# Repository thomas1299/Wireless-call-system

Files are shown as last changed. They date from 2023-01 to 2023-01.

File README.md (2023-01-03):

# Wireless-call-system
Die drahtlos angesteuerte Rufanlage dient zum Absetzen eines Notrufs, welche speziell für Menschen mit Einschränkungen der oberen Gliedmaßen entwickelt wurde. Anstatt wie bei herkömmlichen Rufanlagen, wo eine Taste gedrückt werden muss, um den Alarm auszulösen, erfolgt bei dieser Rufanlage die Alarmauslösung über Messung der Temperatur. Die Rufanlage ist in der Lage durch Messung der Temperatur zu erkennen, ob der Sensor zwischen die Lippen genommen wurde oder nicht, um so einen Alarm auszulösen. Der Alarm wird am Basisgerät, an welchem der Temperatursensor angeschlossen ist und am mobilen Empfangsgerät ausgelöst.

Die Alarmauslösung auf beiden Geräten erfolgt innerhalb von 500 ms ab dem Berühren des Sensors durch die Lippen und die Reichweite der Funkverbindung beträgt mindestens 100 m im Freien. Beide Geräte können mit einem Li-Ionen-Akku der Größe 18650 mit 3,7 V versorgt werden.

Die Rufanlage wurde so entwickelt dass diese möglichst Kostengünstig und einfach nachzubauen ist.

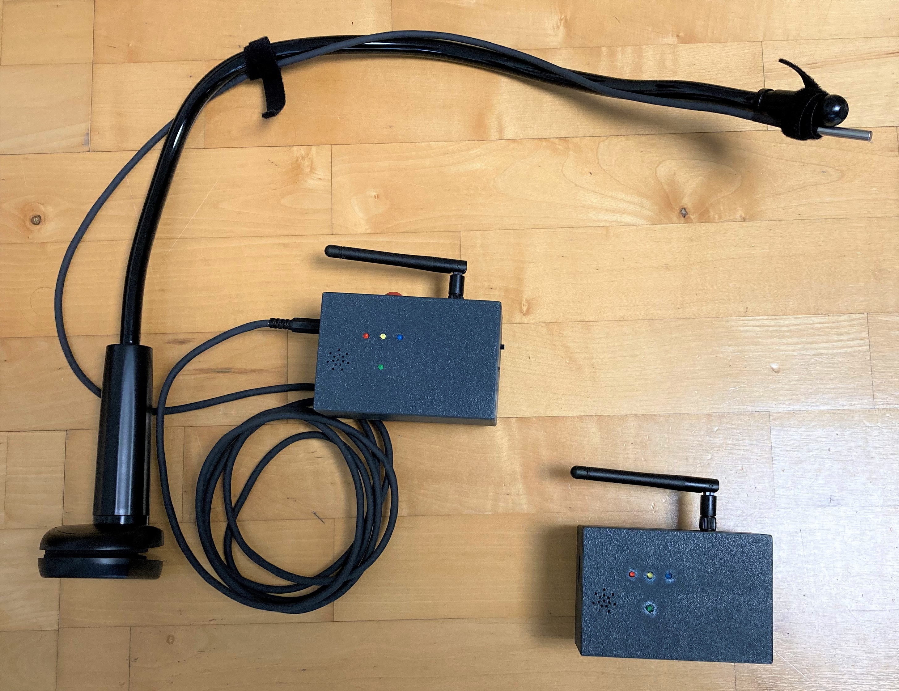
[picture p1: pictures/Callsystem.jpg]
Callsystem


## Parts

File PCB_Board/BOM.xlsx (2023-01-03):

Comment | Designator | Footprint | LCSC
Buzzer | BZ1 | Buzzer_Beeper:Buzzer_12x9.5RM7.6 | C96222
100nF | C2,C3 | Capacitor_SMD:C_0805_2012Metric | C49678
10uF | C4 | Capacitor_SMD:C_0805_2012Metric | C15850
22uF | C5,C6 | Capacitor_SMD:C_1206_3216Metric | C12891
Red | D5 | LED_SMD:LED_0805_2012Metric | C84256
Blue | D6 | LED_SMD:LED_0805_2012Metric | C34499
SS54 | D7 | Diode_SMD:D_SMA | C22452
SS34 | D8 | Diode_SMD:D_SMA | C8678
DW01A-G | IC1 | Package_TO_SOT_SMD:SOT-23-6 | C61503
TYPE-C-31-M-17 | J1 | project_library:TYPEC31M17_new | C283540
Conn_01x04_Male | J3 | Connector_PinHeader_2.54mm:PinHeader_1x04_P2.54mm_Vertical | C2905435
TP4056 | J5 | project_library:SOP127P600X175-9N | C16581
Jumper_2_Bridged | JP1 | Connector_PinHeader_2.54mm:PinHeader_1x02_P2.54mm_Vertical | C234182
22uH | L1 | project_library:SLO0630H | C207843
2N7002 | Q1 | Package_TO_SOT_SMD:SOT-23 | C8545
SI2301CDS-T1-GE3 | Q2 | Package_TO_SOT_SMD:SOT-23 | C10487
FS8205 | Q3 | Package_TO_SOT_SMD:SOT-23-6 | C908265
AO3401A | Q4 | Package_TO_SOT_SMD:SOT-23 | C15127
100k | R1,R3,R4,R17 | Resistor_SMD:R_0805_2012Metric | C149504
10k | R11 | Resistor_SMD:R_0805_2012Metric | C17414
1,2k | R12 | Resistor_SMD:R_0805_2012Metric | C17379
100 | R16 | Resistor_SMD:R_0805_2012Metric | C17408
2,2k | R18 | Resistor_SMD:R_0805_2012Metric | C17520
1M | R2 | Resistor_SMD:R_0805_2012Metric | C17514
5,1k | R5,R6,R10 | Resistor_SMD:R_0805_2012Metric | C27834
1k | R7,R8,R13,R14,R15 | Resistor_SMD:R_0805_2012Metric | C17513
4,7k | R9 | Resistor_SMD:R_0805_2012Metric | C17673
100k | RV1 | Potentiometer_THT:Potentiometer_Bourns_3296W_Vertical | C118963
SW_Push | SW1 | Connector_PinHeader_2.54mm:PinHeader_1x02_P2.54mm_Vertical | C234182
SW_SPST | SW2 | Connector_PinHeader_2.54mm:PinHeader_1x02_P2.54mm_Vertical | C234182
NRF24L01_Breakout | U1 | project_library:nRF24L01_LNA_Module | C239344
MT3608 | U4 | Package_TO_SOT_SMD:SOT-23-6 | C84817

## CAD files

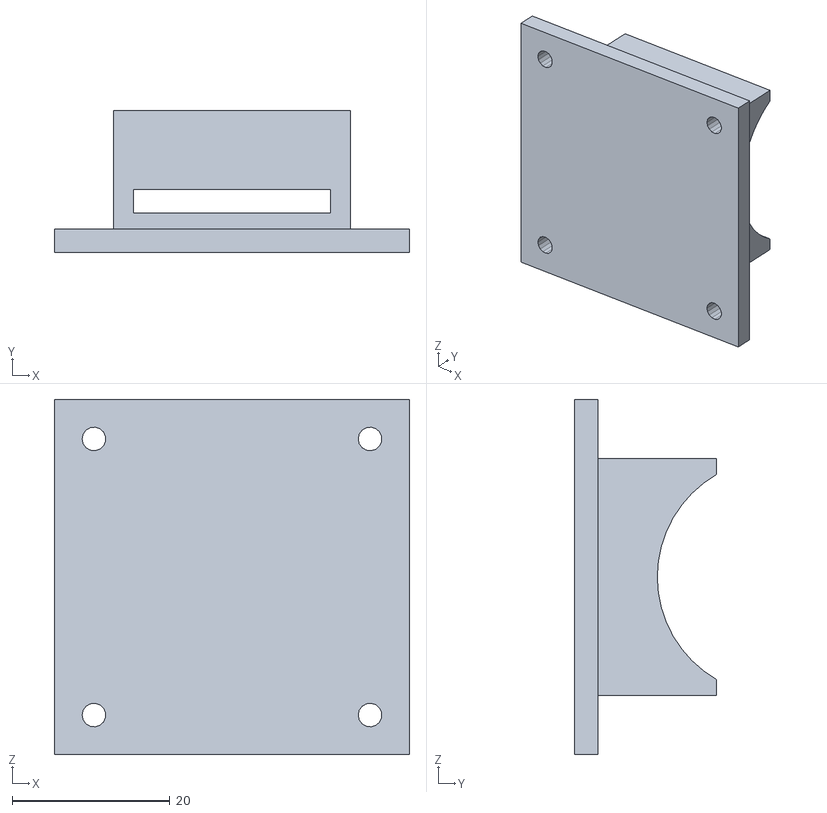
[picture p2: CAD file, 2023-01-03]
3D_Files/print_files/fastening-clip.stl
45.0 x 18.0 x 45.0

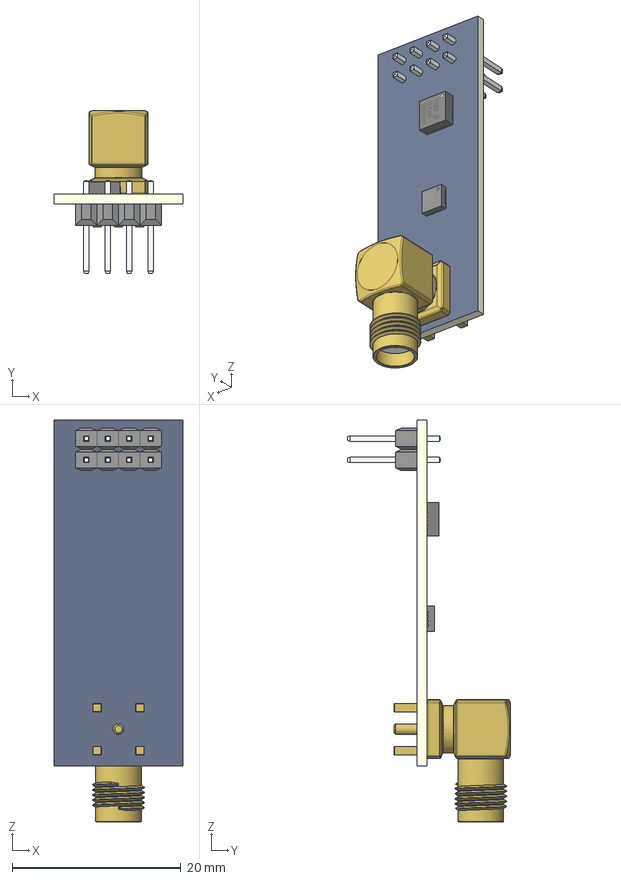
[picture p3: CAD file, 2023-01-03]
PCB_Board/project_libraries/projec_3dmodels/NRF24_module/3d-model/NRF24l01_without_antenna.stp
15.2 x 19.3 x 47.6 mm
NRF24L01_PCB
male header x 8
NRF24L01_SMA-angled
NRF24L01-CHIP-NRF___ _________
User Library-QFN-16_3x3_1
User Library-QFN-16_3x3_2
User Library-QFN-16_3x3_3
User Library-QFN-16_3x3_4
User Library-QFN-16_3x3_5
User Library-QFN-16_3x3_6
User Library-QFN-16_3x3_7
User Library-QFN-16_3x3_8
User Library-QFN-16_3x3_9
User Library-QFN-16_3x3_10
User Library-QFN-16_3x3_11
User Library-QFN-16_3x3_12
User Library-QFN-16_3x3_13
User Library-QFN-16_3x3_14
User Library-QFN-16_3x3_15
User Library-QFN-16_3x3_16
User Library-QFN-16_3x3_17
User Library-QFN-16_3x3_18

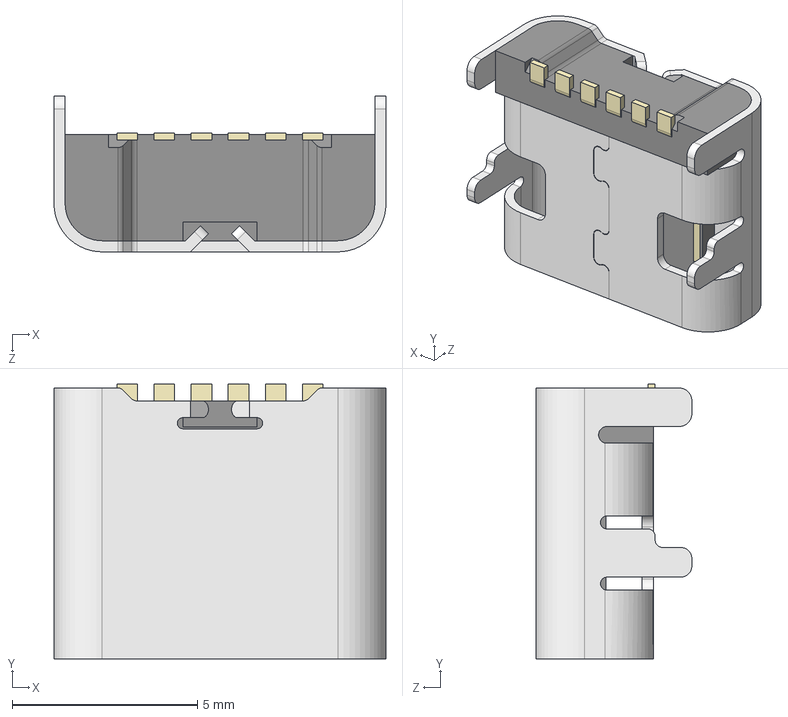
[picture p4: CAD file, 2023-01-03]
PCB_Board/project_libraries/projec_3dmodels/TYPE-C-31-M-17/TYPE-C-31-M-17.stp
8.95 x 7.40 x 4.20 mm

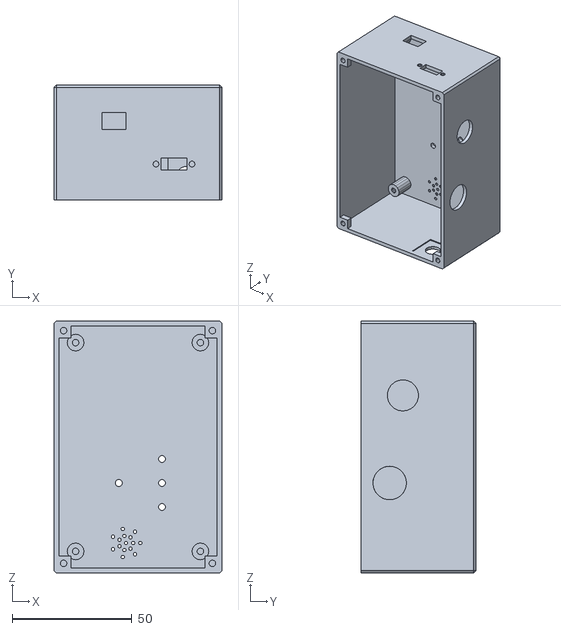
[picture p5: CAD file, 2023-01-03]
3D_Files/print_files/Top_basestation.stl
70.0 x 48.0 x 105.0

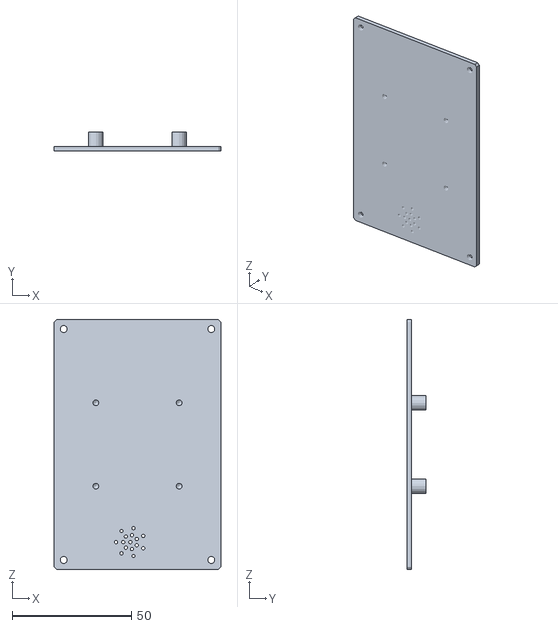
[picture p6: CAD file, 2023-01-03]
3D_Files/print_files/Case_bottom.stl
70.0 x 8.00 x 105.0

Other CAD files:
3D_Files/print_files/Top_handheld.stl
3D_Files/Case_bottom.ipt
3D_Files/Top_basestation.ipt
3D_Files/Top_handheld.ipt
3D_Files/fastening-clip.ipt
PCB_Board/project_libraries/projec_3dmodels/NRF24_module/3d-model/NRF24l01_without_antenna.iam

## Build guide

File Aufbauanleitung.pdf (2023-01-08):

# Aufbauanleitung der Rufanlage

## Inhalt

Dies ist eine Schritt-für-Schritt-Anleitung, um die drahtlos angesteuerte Rufanlage, bestehend aus dem Basisgerät und dem Empfangsgerät, nachbauen zu können. Der Schaltplan der Platine (Callsystem.pdf) befindet sich im Ordner „PCB_Board“.

### 1. Werkzeugliste

Zum Aufbau der Rufanlage werden folgende Werkzeuge benötigt:
- Lötkolben + Lötzinn
- Seitenschneider
- Flachzange oder Kombizange
- Heißklebepistole
- Multimeter
- Heißluftfön (alternativ Feuerzeug)
- Evtl. Bohrmaschine
- Kreuzschlitzschraubendreher PZ1

### 2. Bauteilliste

Folgende Komponenten sind erforderlich, für den Nachbau der drahtlos angesteuerte Rufanlage:

Teil | Lieferant | Bestellnummer | Stück
Arduino Nano | Amazon | Amazon-Link (https://www.amazon.de/AZDelivery-Atmega328-gratis-Arduino-kompatibel/dp/B078SBBST6?adgrpid=73713830840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) | 2
Bestückte Platine (PCB) | JLCPCB | https://jlcpcb.com/ | 2
18650 Akkuhalterung | Amazon | Amazon-Link (https://www.amazon.de/Haljia-18650-Batterie-Halterung-Kunststoff-Stift/dp/B07MM1NHHL?__mk_de_DE=%C3%85M%C3%85%C5%BD%C3%95%C3%91) | 2
Li-Ion Akku 18650 3,7V-3000mAh | Amazon | Amazon-Link (https://www.amazon.de/Wiederaufladbarer-POWO18B-Knopfbatterien-Taschenlampe-batteriebetriebene-Red/dp/B09KZGQSJJ) | 2
RF24L01+PA+LNA-Funkmodul | Amazon | Amazon-Link (https://www.amazon.de/-/en/DollaTek-2-Piece-NRF24L01-Antistatic-Compatible/dp/B07PQPFTWZ) | 2
Schiebeschalter | Amazon | Amazon-Link (https://www.amazon.de/-/en/gp/product/B07Z4RW9X6/ref=ppx_od_dt_b_asin_title_s00?ie=UTF8&psc=1) | 2
Klettband | Conrad | 536744 – U3 | 2

LED Rot 3mm | Conrad | 1603079 – U3 | 2
LED Gelb 3mm | Conrad | 1577458 – U3 | 2
LED Blau 3mm | Conrad | 1577321 – U3 | 2
LED Grün 3mm | Conrad | 1577354 – U3 | 2
Buchsenleiste 15-polig | Conrad | 1492307 – U3 | 4
4-poliger 3,5mm Klinkenstecker | Amazon | Amazon-Link (https://www.amazon.de/gp/product/B08DTC33XC/ref=ppx_od_dt_b_asin_title_s03?ie=UTF8&psc=1) | 1
4-poliger 3,5mm Klinkensteckerbuchse | Amazon | Amazon-Link (https://www.amazon.de/gp/product/B089222S84/ref=ppx_od_dt_b_asin_title_s03?ie=UTF8&psc=1) | 1
TSic506 Temperatursensor | Conrad | 506360 – U3 | 1
Edelstahlhülse | Conrad | 156557 – U3 | 1
4-poliges Kabel (2 Meter) | Conrad | 457980 – U3 | 1
Wärmeleitkleber | Amazon | Amazon-Link (https://www.amazon.de/gp/product/B00XQ9AZ8Y/ref=ppx_od_dt_b_asin_title_s00?ie=UTF8&th=1) | 1
Schwanenhals | Amazon | Amazon-Link (https://www.amazon.de/gp/product/B00XQ9AZ8Y/ref=ppx_od_dt_b_asin_title_s00?ie=UTF8&th=1) | 1
Taster | Amazon | Amazon-Link (https://www.amazon.de/gp/product/B0825RCZJS/ref=ppx_od_dt_b_asin_title_s01?ie=UTF8&psc=1) | 1
Schrumpfschlauch ø 2,5 mm | Conrad | 1572501 - U3 | 0,2
Schrumpfschlauch ø 5 mm | Conrad | 1571367 - U3 | 0,2
Schrauben ISO7049 2,9x9,5mm | Conrad | 147586 – U3 | 24
Schaltdraht ø0,2mm² verschiedene Farben | Conrad | 1567887 - U3 | 5m

Folgende Teile aus dem Ordner (3D_Files\print_files) müssen mit einem 3D-Drucker ausgedruckt werden:
Teil | Stück
Case_bottom | 2
Top_basestation | 1
Top_handheld | 1
Fastening-clip | 2

### 3. Leiterplattenbestellung

Für beide Geräte wurde eine Platine entwickelt, die in beiden Geräten eingebaut wird. Die vorbestückte Platine muss von einem Leiterplattenhersteller produziert werden. Vorzugsweise sollte die Platine beim Hersteller „JLCPCB“ (https://jlcpcb.com/) bestellt werden, weil die im Projektordner enthaltene Bauteilliste auf dem Teilekatalog dieses Herstellers basiert. Sollte die Platine bei einem anderen Hersteller bestellt werden, so ist darauf zu achten, dass die Bauteilliste (BOM) des Projektes auf die verfügbaren Bauteile dieses Herstellers angepasst werden.

Um die Platine bestellen zu können, werden folgende Dateien aus dem Ordner „PCB_Board“ benötigt:
- Gerber.zip (Gerber-Dateien)
- BOM.xlsx (Bauteilliste inkl. Teilenummer)
- CPL.xlsx

Bestellablauf:
1. Zuerst einen Account bei JLCPCB erstellen (https://jlcpcb.com/)

2. Nachdem der Account erstellt wurde, klicken Sie auf die Schaltfläche „Order now“.
3. Auf die blaue Schaltfläche „Add Gerber File“ klicken und das Archiv „Gerber.zip“ hochladen. Nach dem Hochladen wird die Platine am Bildschirm angezeigt. Nun weiter nach unten scrollen bis zum „PCB-Assembly“; die Einstellungen müssen nicht angepasst werden.

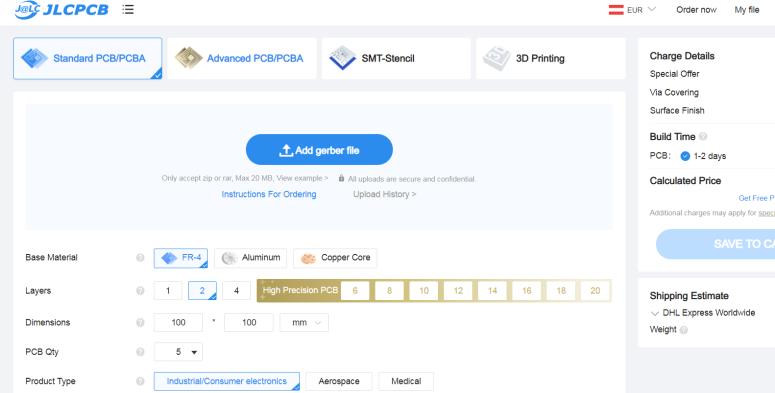
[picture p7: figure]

4. Die Schaltfläche für „PCB-Assembly“ aktivieren (roter Pfeil im Bild). Wenn alle Einstellungen wie im Bild aktiviert sind, drücken Sie auf die Schaltfläche „Confirm“.

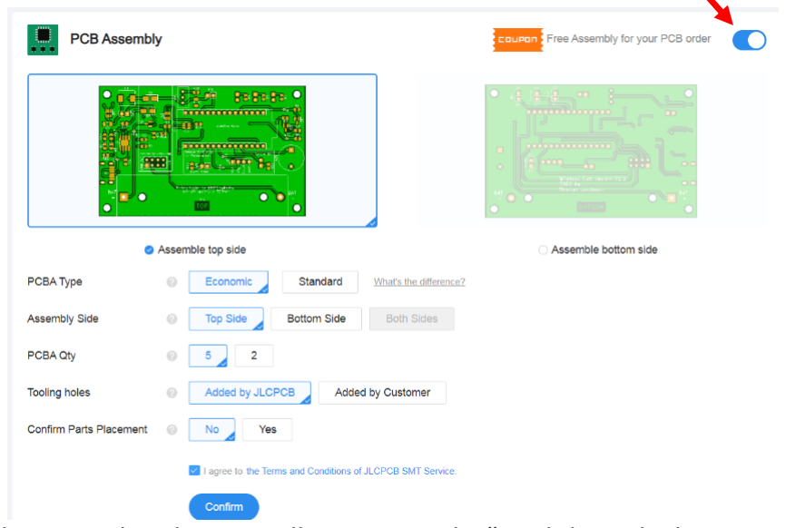
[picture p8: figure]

5. Im nächsten Schritt werden die Bauteilliste „BOM.xlsx“ und die Bohrdatei „CPL.xlsx“ aus dem Projektordner „PCB_Board“ hochgeladen.
6. Im Anschluss muss eine Beschreibung für das Produkt eingegeben werden. Dazu die Kategorien „Research\Education\DIY\Entertainment“ und „Others“ auswählen und eine kurze Beschreibung eintippen ( z.B. Rufanlage). Um fortzufahren klicken Sie auf die Schaltfläche „Next“.

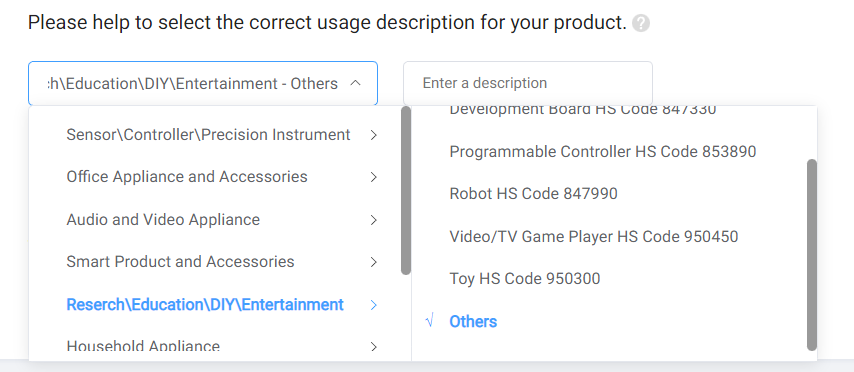
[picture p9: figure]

7. Im nächsten Schritt werden alle Bauteile aus der Bauteilliste aufgelistet; sollten keine Fehler angezeigt werden, kann zum nächsten Schritt übergegangen werden. Sollten etwaige Bauteile nicht mehr verfügbar sein, müssen andere Bauteile verwendet werden. Dazu muss die Bauteilliste „BOM.xlsx“ geändert werden. Um alternative Bauteile auswählen zu können, müssen diese im Teilekatalog des Herstellers gesucht und die Bauteilenummer (LCSC-Nummer) in die Bauteilliste eingetragen werden. Zum Aktualisieren der neuen Bauteile muss Schritt 6 wiederholt werden.
8. In diesem Schritt wird die Platine mit platzierten Komponenten und den gesamten Kosten angezeigt. Sollten die Komponenten nicht ordentlich platziert worden sein, können diese mit einem Klick auf die rot eingekreiste Schaltfläche automatisch angeordnet werden. Mit einem Klick auf „Save to Cart“ wird die Platine mit den Komponenten in den Einkaufswagen gelegt.

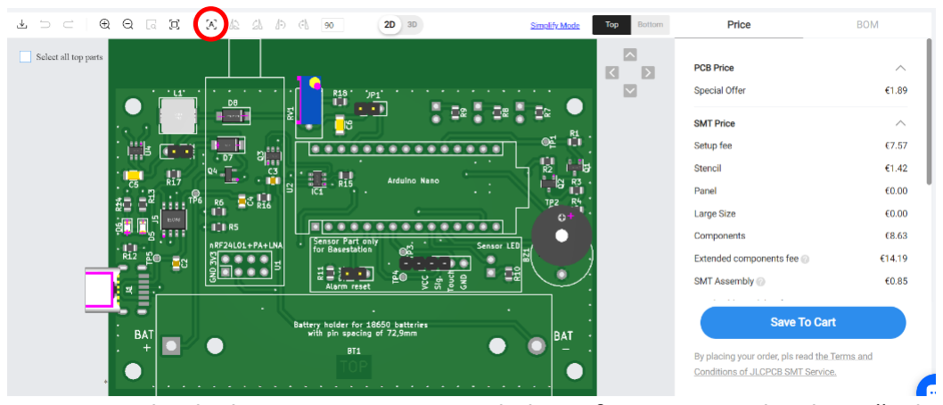
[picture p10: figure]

9. Im geöffneten Warenkorb kann mit einem Klick auf „Secure Checkout“ die Bestellung abgeschlossen werden.

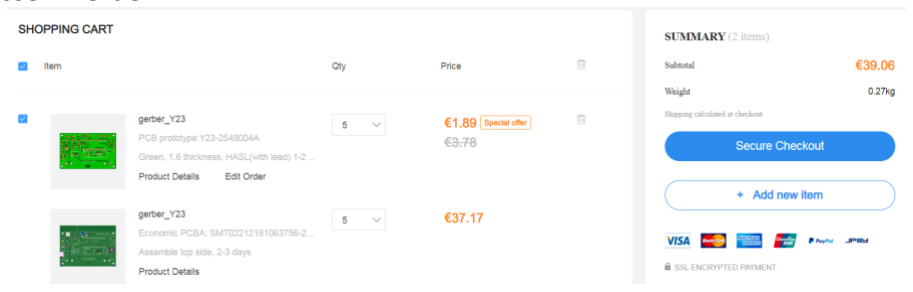
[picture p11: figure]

### 4. Programmieren beider Mikrocontroller 4.1. Vorbereitungen der Entwicklungsumgebung

1) Downloaden und Installieren der aktuellen Arduino IDE https://www.arduino.cc/en/software
2) Die Arduino Entwicklungsumgebung starten
3) Installieren der benötigten Librarys
- Tools > Manage Libraries…
- Nach „RF24“ suchen und die Library von TMRh20 installieren

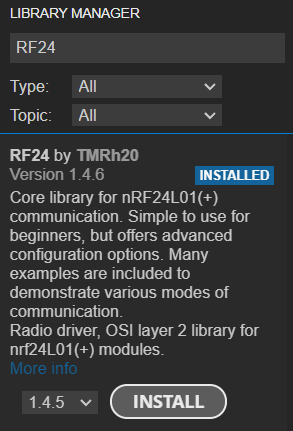
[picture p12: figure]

4) Die Ordner der Firmware für beide Geräte aus dem Repository downloaden.
- SW_Basestation
- SW_Handheld

### 4.2. Programmierung der Mikrocontroller

Zum Programmieren der beiden Arduino Nanos wird ein USB-Kabel mit USB-Mini-B-Stecker benötigt. Der Ablauf der Programmierung erfolgt für beide µC gleich, jedoch werden unterschiedliche Firmwares für die beiden Geräte verwendet.

1) Öffnen der SW_Basisstation.ino bzw. SW_Handheld.ino Firmware
2) Board aus der Boardliste auswählen
- Tools>Board> Arduino AVR Boards > Arduino Nano

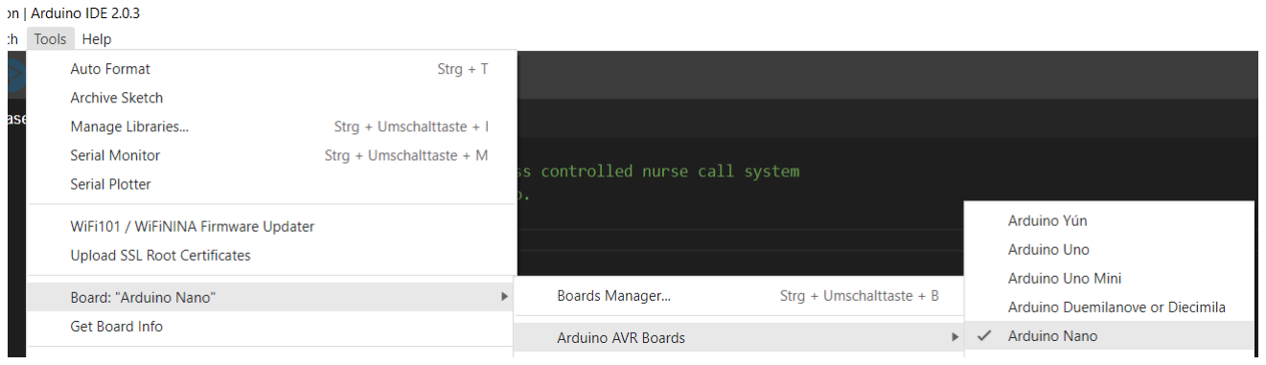
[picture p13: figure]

3) Arduino über ein USB-Kabel mit dem Computer verbinden und den Port auswählen.
- Tools > Port > „Port“ (Portnummer kann unterschiedlich sein)
4) Mit einem Klick auf „Verify“ prüfen, ob die Firmware kompiliert werden kann.
5) Mit Klick auf den „Upload“ Button wird die Firmware auf dem Arduino programmiert.

Nach dem Programmieren kann der Arduino vom Computer getrennt und auf die Platine gesteckt werden.

### 5. Aufbau der Rufanlage

Nachdem alle benötigten Teile geliefert worden sind, kann mit dem Aufbau der Rufanlage begonnen werden. Der prinzipielle Aufbau beider Geräte ist identisch, jedoch werden beim Basisgerät zusätzlich ein Taster sowie die Klinkensteckerbuchse für den Sensor eingebaut.

Um Energie während des Betriebs zu sparen, wird auf beiden Mikrocontrollern der Vorwiderstand der Power LED ausgelötet (siehe rot markierter Bereich im folgenden Bild).

Schritt 1) Zuerst werden die beiden Buchsenleisten und danach die Akkuhalterungen auf die Platinen gelötet.

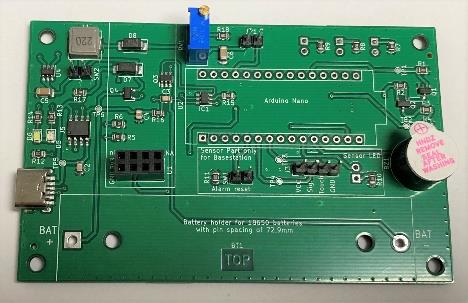
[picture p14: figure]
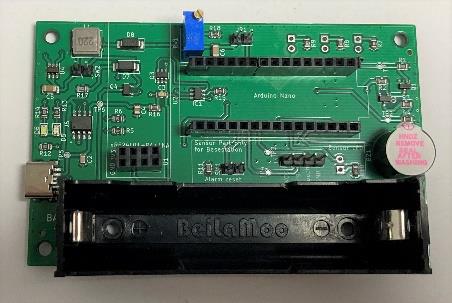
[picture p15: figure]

Schritt 2) Alle 4 LEDs (blau, gelb, grün, rot) müssen für den Einbau in das Gehäuse vorbereitet werden, damit die Anschlussdrähte keinen Kurzschluss auf der Platine verursachen. Für die elektrische Verbindung müssen 8 Drähte (4x rot / 4x schwarz) mit je einer Länge von 17 cm vorbereitet werden. Zuerst wird mit einer Zange die Kathode (kürzeres Bein „-“Pol) bei jeder LED umgebogen. Die umgebogenen Beine werden kurz nach der Biegung abgetrennt und dort die schwarzen Drähte angelötet. Der andere Anschluss, die Anode, der LED, wird in die gegenüberliegende Richtung gebogen und ebenfalls gekürzt. An diesen Anschlüssen werden die roten Drähte angelötet.

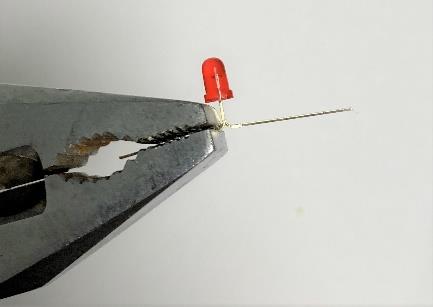
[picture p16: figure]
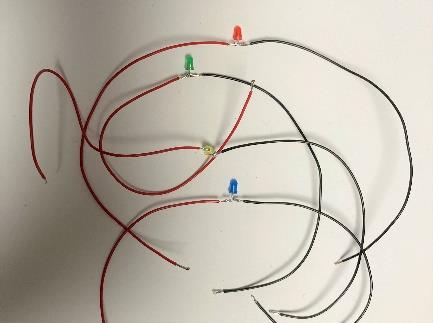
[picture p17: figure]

Schritt 3) Die Anschlussdrähte der LEDs werden nun an die Unterseite der Platine gelötet, dabei sollte die Beschriftung auf der Platine beachtet werden.

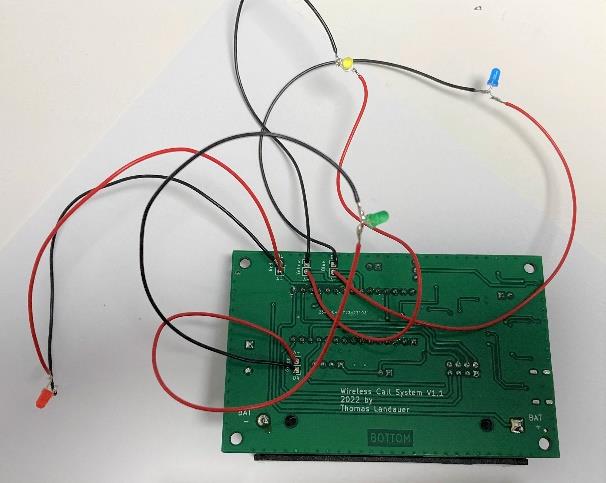
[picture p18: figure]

Schritt 4) In diesem Schritt werden nun die LEDs in das Gehäuse an die vorgesehene Position gesetzt und mit der Heißklebepistole fixiert. Sollten die LEDs nicht in die Löcher passen, muss dieses mit einem 3 mm Bohrer aufgebohrt werden. Beim Einkleben ist darauf zu achten, dass die Anschlussdrähte vollständig vom Kleber bedeckt sind. Die Reihenfolge, in der die LEDs von links beginnend eingeklebt werden, ist: rot, gelb, blau. Nachdem die LEDs eingeklebt sind, kann die Platine in das Gehäuse gesetzt und mit 4 Schrauben festgeschraubt werden.

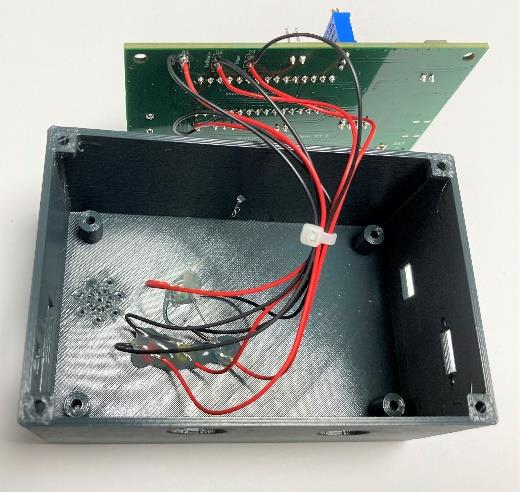
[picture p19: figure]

Schritt 5) Jetzt wird der Ein- und Ausschalter für den Einbau vorbereitet. Dazu werden 2 Drähte mit je 7 cm Länge wie im Bild dargestellt an 2 Anschlüsse des Schalters gelötet.

Die beiden Drahtenden werden anschließend auf die Stiftleiste mit der Bezeichnung „SW2“ gelötet. Nach dem Löten wird der Schalter mit der Heißklebepistole an die Wand des Gehäuses geklebt.

Sobald der Ein- und Ausschalter in das Gehäuse geklebt wurde, ist der Aufbau des Empfängergerätes abgeschlossen.

Alle weiteren Schritte betreffen nur das Basisgerät.

Schritt 6) Für den Einbau der Klinkenstecker-Buchse werden 3 Drähte mit einer Länge von 7 cm benötigt. Die Drähte werden entsprechend dem Schaltplan an die Klinkenstecker-Buchse (J2) angelötet. Um ein Vertauschen der Anschlüsse zu vermeiden, sollte der Klinkenstecker in die Buchse gesteckt und mit einem Multimeter durchgemessen werden. Nachdem die Drähte an die Buchse gelötet wurden, kann die Klinkenstecker-Buchse in das Gehäuse eingebaut und die Drähte an die Stiftleiste J3 gelötet werden. Sollte die Buchse nicht in die Öffnung im Gehäuse passen, so muss diese mit einem geeigneten Bohrer aufgebohrt werden.

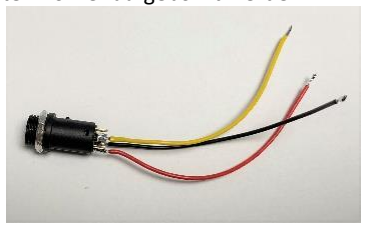
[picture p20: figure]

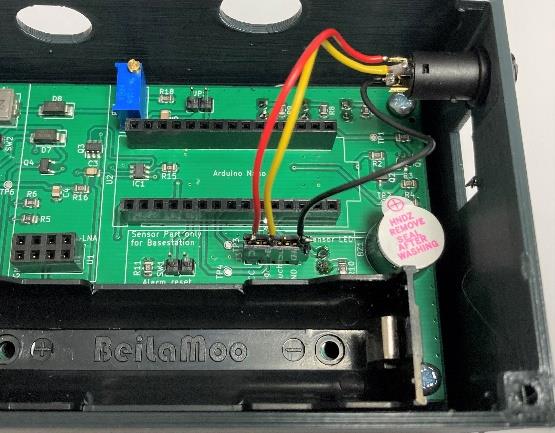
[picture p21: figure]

Schritt 7) In diesem Schritt erfolgt der Einbau des Tasters. Zuerst wird der Taster zerlegt und beide Drähte auf 8 cm gekürzt. Anschließend wird der Taster am Gehäuse befestigt und danach werden die Drähte an die Stiftleisten mit der Bezeichnung SW1 gelötet. Somit sind nun beide Platinen vollständig bestückt.

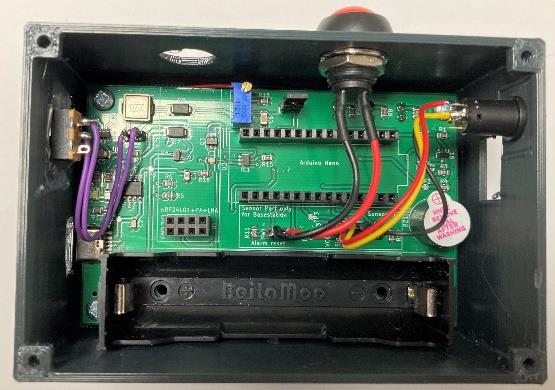
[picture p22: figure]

### 5.1. Einkleben des Sensors

Damit der Sensor verwendet werden kann, muss dieser zunächst in eine Edelstahlhülse geklebt und an ein Kabel gelötet werden. Die Länge des Kabels kann individuell festgelegt werden. Eine Länge von 2-3 Metern ist ausreichend.

Für die Montage des Sensors werden folgende Teile benötigt:
- TSic506-Sensor
- Edelstahlhülse
- Wärmeleitkleber
- Klinkenstecker
- Kabel
- Schrumpfschläuche

Schritt 1) Zuerst den Klinkenstecker zerlegen und den Knickschutz auf das Kabel schieben. Danach den Mantel des Kabels auf einer Länge von max. 1 cm abisolieren (die einzelnen Drähte
sollten | möglichst | kurz | sein, | da | ansonsten | der | Einbau | schwieriger | wird).
Den Kabelschirm entflechten, auf eine Seite führen und dann verdrillen. Im Anschluss 3 Drähte abisolieren und verzinnen; der vierte Draht kann abgeschnitten werden, weil dieser nicht benötigt wird. Danach den verdrillten Kabelschirm durch die Bohrung des Steckers führen, umknicken und dann verlöten. Die Zugentlastungslaschen des Klinkensteckers müssen den Mantel vollständig überdecken (roter Kreis in den Bildern)!

Danach die 3 Drähte entsprechend dem Schaltplan an die Laschen des Klinkensteckers löten.

Nach dem Löten die einzelnen Leitungen mit einem Durchgangsprüfer auf Kurzschlüsse überprüfen! Wenn keine Kurzschlüsse vorhanden sind, können die Zugentlastungslaschen mit einer Zange auf das Kabel gepresst werden und im Anschluss der Knickschutz wieder angeschraubt werden.

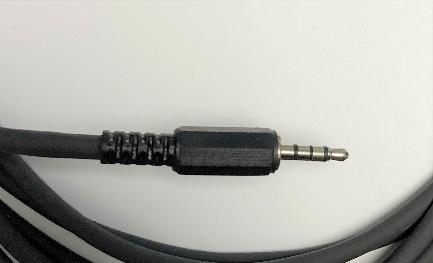
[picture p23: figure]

Schritt 2) Nun wird der Sensor an das Kabel gelötet. Dazu muss ebenfalls der Mantel des Kabels auf einer Länge von ca. 1 cm abisoliert werden. Der Kabelschirm und der nicht benötigte Draht können abgeschnitten werden. Die Anschlussdrähte des Sensors werden ebenfalls gekürzt. Die beiden größeren Schrumpfschläuche werden vor der Montage auf das Kabel geschoben. Danach
werden | die | einzelnen | Drähte | abisoliert | und | mit | Lötzinn | verzinnt.
Bevor mit dem Löten des Sensors begonnen wird, sollte die korrekte Verkabelung mit einem Multimeter (Durchgangsprüfer) überprüft werden. Dazu das Kabel am Basisgerät einstecken und mit dem Multimeter auf der Platine (Stifleiste J3) und am Kabelende auf Durchgang prüfen. Das Ergebnis der Messung auf einem Blatt notieren.

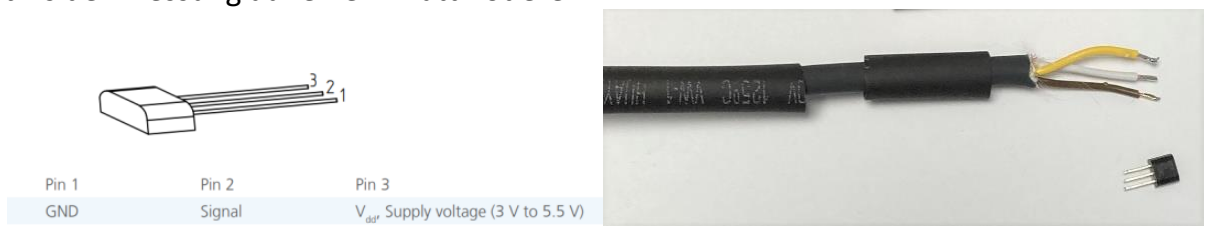
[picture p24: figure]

Bevor der Sensor an das Kabel gelötet werden kann, muss auf jedem Kabel ein kurzes Stück Schrumpfschlauch aufgeschoben werden. Danach kann der Sensor entsprechend der Schaltung und dessen Anschlussbelegung auf das Kabel gelötet werden. Nach dem Löten werden die Schrumpfschläuche über die Lötstellen geschoben und mit einem Heißluftfön oder vorsichtig mit einem Feuerzeug aufgeschrumpft. Im Anschluss wird der ø 2,5 mm Schrumpfschlauch wie im Bild dargestellt nach vorne gezogen und ebenfalls geschrumpft. Dieser Schrumpfschlauch ist nötig, damit das Kabel besser in der Edelstahlhülse sitzt.

Schritt 3) In diesem Schritt erfolgt das Einkleben des Sensors. Bevor mit dem Einkleben begonnen werden kann, wird der Schrumpfschlauch mit ø 5 mm über das Kabel gezogen. Im

Anschluss wird die Edelstahlhülse bis zur Hälfte mit dem Wärmeleitkleber befüllt. Nach dem Befüllen der Hülse wird der Sensor in die Hülse hineingeschoben, bis dieser den Boden der Hülle berührt. Nun muss circa 30 Minuten gewartet werden, bis der Kleber ausgehärtet ist; dabei sollte der Sensor nicht bewegt werden. Am besten ist es, wenn die Hülse und das Kabel mit Klebeband fixiert werden. Nachdem der Kleber ausgehärtet ist, kann der Schrumpfschlauch über Hülse und Kabel geschoben und geschrumpft werden. Dieser Schrumpfschlauch bietet zusätzlichen Schutz gegen Knicken und das Eindringen von Wasser.

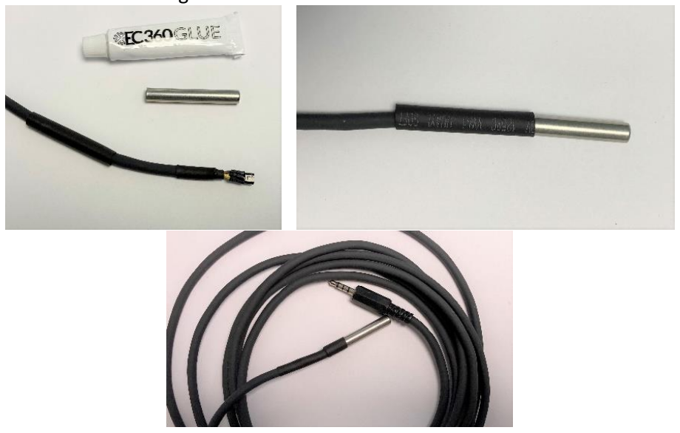
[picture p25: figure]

### 5.2. Einstellen des Step-Up-Converters

Bevor der Mikrocontroller und das Funkmodul eingesetzt werden können, muss die Spannung des Step-Up-Converters bei beiden Geräten eingestellt werden. Dazu muss der Akku richtig eingesetzt werden. Der Pluspol des Akkus auf der Seite des Ein- und Ausschalters und der Minuspol auf der Seite des Buzzers. Nachdem der Akku eingesetzt ist, muss das Gerät über den Ein- und Ausschalter eingeschaltet werden.
Mit einem Multimeter wird nun die Spannung am linken Pin von der Stiftleiste JP1 gegen Masse (GND) gemessen. Nun wird mit einem Schraubendreher der Widerstand des Potentiometers verändert, bis das Multimeter 5 V anzeigt (gegen den Uhrzeigersinn, um die Spannung zu erhöhen, im Uhrzeigersinn, um die Spannung zu verringern).
Nachdem die Spannung auf 5 V eingestellt ist, können die beiden Pins von der Stiftleiste JP1 durch Löten verbunden werden.

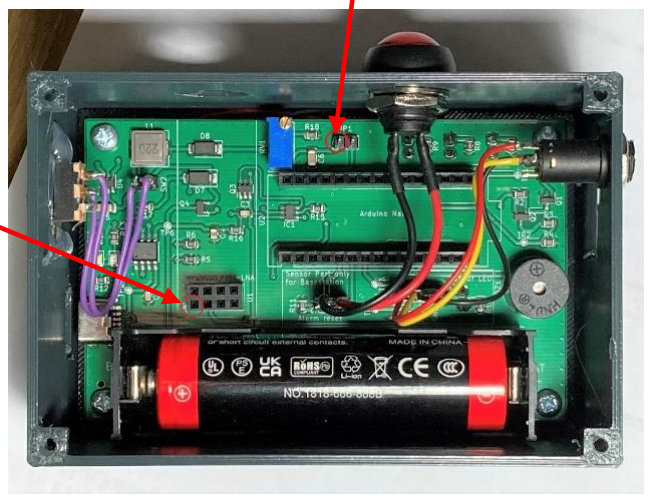
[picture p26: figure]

### 5.3. Einsetzen des Arduinos und des Funkmoduls

Nachdem bei beiden Geräten der Step-Up-Converter eingestellt wurde, können die Mikrocontroller und die nRF-Funkmodule eingesteckt werden.

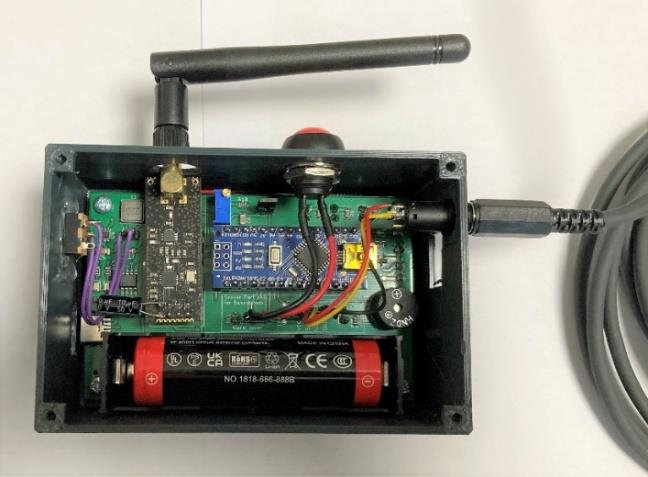
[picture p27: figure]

Nach dem Einsetzen der Komponenten kann das Gehäuse geschlossen werden. Dazu werden je Gerät 8 Stk. Schrauben und der gedruckte Gehäuseboden sowie der Befestigungsclip benötigt. Bei der Positionierung des Bodens ist darauf zu achten, dass die Bohrungen für den Buzzer über diesem sind. Der Befestigungsclip kann wie unterhalb im linken Bild dargestellt oder um 90 ° gedreht montiert werden. Am Ende wird noch die Antenne auf das Funkmodul geschraubt.

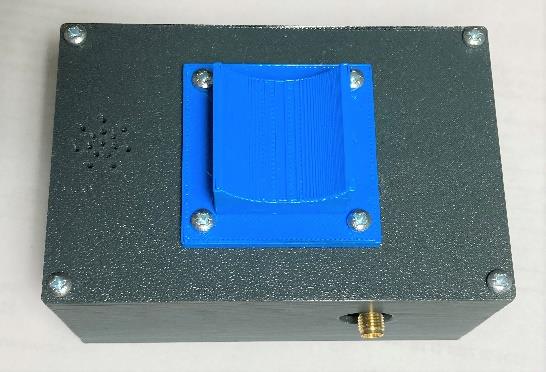
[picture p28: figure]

### 6. Montage am Bett

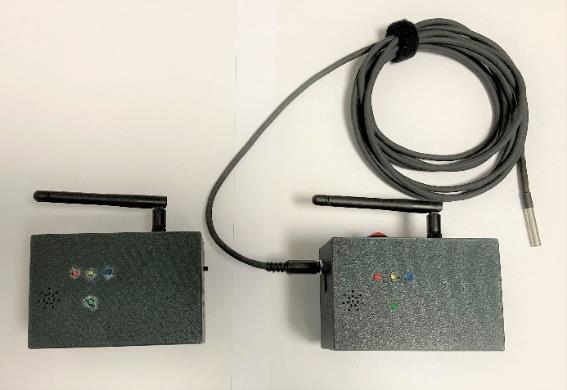
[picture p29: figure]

Das Kabel des Sensors kann wie unten im Bild dargestellt mittels Klettverschlüssen oder z.B. Kabelbindern am Schwanenhals befestigt werden. Der Schwanenhals selbst wird mit dessen Befestigungsgriff am Bett so befestigt, dass der Sensor in die Nähe des Mundes gebracht werden kann. Das Basisgerät kann über den Befestigungsclip und Klettverschluss am Bettgestänge angebracht werden.

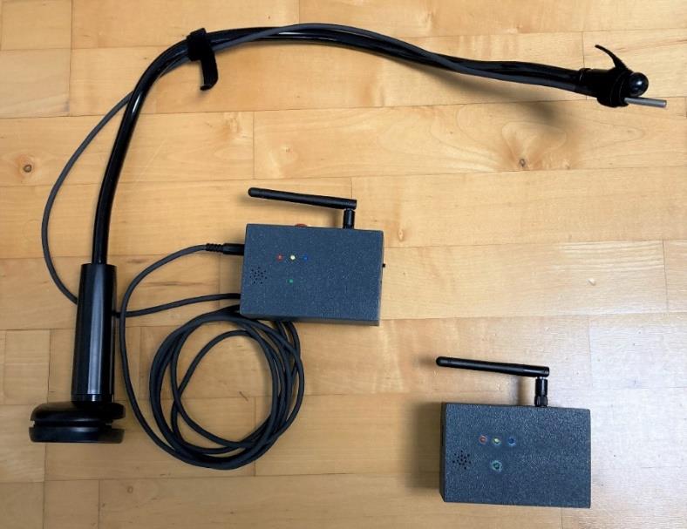
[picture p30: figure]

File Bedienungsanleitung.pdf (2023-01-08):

# Bedienungsanleitung

## Inhalt

Die drahtlos angesteuerte Rufanlage dient zum Absetzen eines Notrufs, welche speziell für Menschen mit Einschränkungen der oberen Gliedmaßen entwickelt wurde. Anstatt wie bei herkömmlichen Rufanlagen, wo eine Taste gedrückt werden muss, um den Alarm auszulösen, erfolgt bei dieser Rufanlage die Alarmauslösung über Messung der Temperatur. Die Rufanlage ist in der Lage durch Messung der Temperatur zu erkennen, ob der Sensor zwischen die Lippen genommen wurde oder nicht, um so einen Alarm auszulösen. Der Alarm wird am Basisgerät, an welchem der Temperatursensor angeschlossen ist und am mobilen Empfangsgerät ausgelöst.

Die Alarmauslösung auf beiden Geräten erfolgt innerhalb von 500 ms ab dem Berühren des Sensors durch die Lippen und die Reichweite der Funkverbindung beträgt mindestens 100 m im Freien. Beide Geräte können mit einem Li-Ionen-Akku der Größe 18650 mit 3,7 V versorgt werden.

### 1. Überblick

Basisgerät:
Das Basisgerät besteht aus dem abnehmbaren Sensor, welcher an der linken Seite des Gerätes angeschlossen wird. An der Oberseite befindet sich der Taster, mit diesem der Alarm quittiert werden kann und die Antenne des Funkmoduls. Auf der Vorderseite befinden sich 4 LEDs, die verschiedene Informationen anzeigen. An der rechten Seite befinden sich der Ein- und Ausschalter sowie eine USB-C Buchse, um das Gerät mit Strom zu versorgen bzw. den eingebauten Akku zu laden. An der Unterseite ist ein Befestigungsclip angebracht, um das Gerät mittels Klettband an einem Bett befestigen zu können.

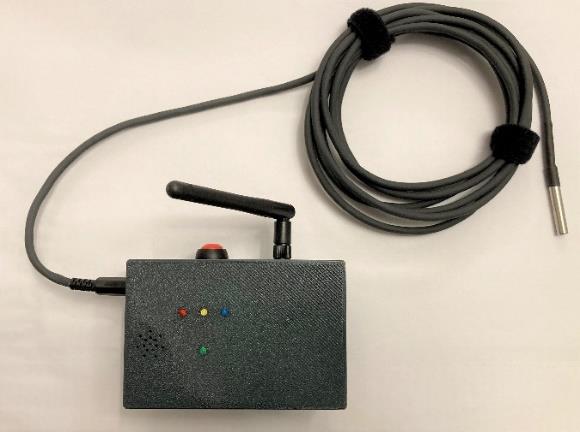
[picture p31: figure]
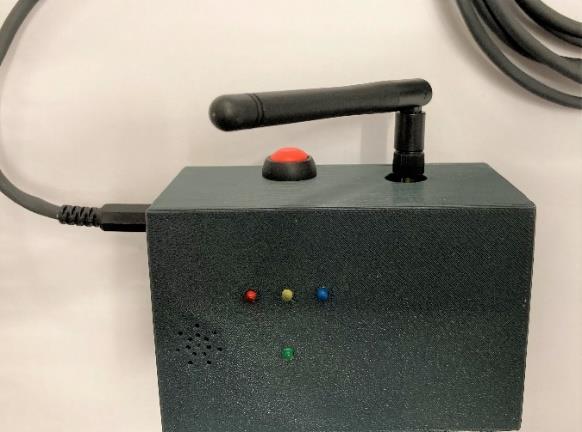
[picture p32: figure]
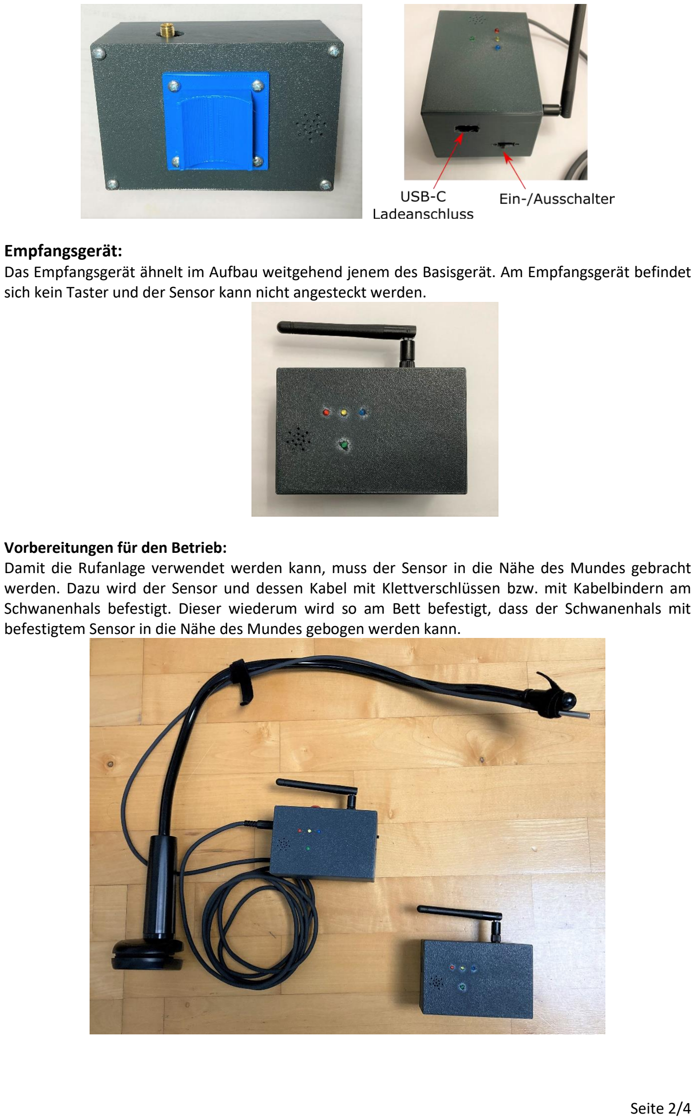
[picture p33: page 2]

Empfangsgerät:
Das Empfangsgerät ähnelt im Aufbau weitgehend jenem des Basisgerät. Am Empfangsgerät befindet sich kein Taster und der Sensor kann nicht angesteckt werden.

Vorbereitungen für den Betrieb:
Damit die Rufanlage verwendet werden kann, muss der Sensor in die Nähe des Mundes gebracht werden. Dazu wird der Sensor und dessen Kabel mit Klettverschlüssen bzw. mit Kabelbindern am Schwanenhals befestigt. Dieser wiederum wird so am Bett befestigt, dass der Schwanenhals mit befestigtem Sensor in die Nähe des Mundes gebogen werden kann.

### 2. Inbetriebnahme

Basisgerät:
Bevor das Gerät eingeschaltet wird, muss kontrolliert werden, ob der Sensor eingesteckt und die Antenne des Funkmoduls montiert ist. Nun kann das Gerät über den seitlich angebrachten Schalter eingeschaltet werden. Nach dem Einschalten werden alle Module initialisiert und auf Funktionstüchtigkeit überprüft. Ist z. B. der Sensor nicht eingesteckt, leuchtet direkt nach dem Einschalten die grüne LED, um einen Sensorfehler anzuzeigen. Erst wenn der Sensor eingesteckt ist und korrekte Werte liefert, erlischt die grüne LED. Erst wenn alle LEDs 3-mal blinken, ist die Initialisierung abgeschlossen und das Gerät betriebsbereit. Im Normalbetrieb leuchten keine LEDs! (In Punkt 3 Statusleuchten / Fehleranzeige wird die Bedeutung der leuchtenden LEDs beschrieben)

Wenn nun der Sensor mit den Lippen berührt wird, erkennt dies das Gerät und löst einen Alarm aus (blinkende rote LED + Buzzer). Der Alarm wird drahtlos an das Empfangsgerät übertragen. Durch Drücken der Taste kann der Alarm für beide Geräte quittiert werden und das Gerät geht in den normalen Betriebsmodus über.

Empfangsgerät:
Bevor das Gerät eingeschaltet wird, muss kontrolliert werden, ob der Sensor eingesteckt und die Antenne des Funkmoduls montiert ist. Nun kann das Gerät über den seitlich angebrachten Schalter eingeschaltet werden. Nach dem Einschalten werden alle Module initialisiert; bei erfolgreicher Initialisierung blinken alle LEDs 3-mal. Danach ist das Gerät betriebsbereit.

Wird ein Alarm vom Basisgerät empfangen, so wird am Empfangsgerät ebenfalls der Alarm ausgelöst (blinkende rote LED + Buzzer). Der Alarm am Basisgerät wird so lange ausgegeben, bis am Basisgerät die Taste gedrückt wird. Damit soll sichergestellt werden, dass die Betreuungsperson nicht auf den Hilferuf vergisst bzw. den Alarm unabsichtlich quittiert.

### 3. Statusleuchten / Fehleranzeige

Während des fehlerfreien Normalbetriebs leuchten auf beiden Geräten keine LEDs.
Die 4 LEDs dienen zum Anzeigen von Fehlzuständen sowie Statusinformationen sowie dem Alarm und haben folgende Bedeutung:
- Eine blinkende rote LED + Buzzer signalisieren den Alarm
- Die gelbe LED signalisiert einen niedrigen Akkustand
- Die grüne LED signalisiert einen Sensorfehler (Sensor nicht angesteckt bzw. eine fehlerhafte Datenübertragung)
- Die blaue LED signalisiert, wenn die Geräte keine Kommunikation aufgebaut haben. Diese wird aktiviert, wenn kein ACK am Basisgerät bzw. wenn keine Nachricht am Empfangsgerät innerhalb des erwarteten Timeslots empfangen wird.
- Das gleichzeitige Leuchten der roten und blauen LED signalisiert einen Fehler des nRF24-Funkmoduls, wenn z.B. dieses nicht verbunden ist oder nicht mehr reagiert. In diesem Fall stoppt das Programm und die Geräte müssen neu gestartet werden.

Wenn während des Betriebs die blaue LED kurz aufleuchtet, zeigt dies einen Übertragungsfehler an. Sollte die blaue LED hingegen dauerhaft leuchten, so besteht keine funktionierende Funkverbindung zum anderen Gerät.
Folgende Ursachen können die Funkverbindung stören:
- Geräte zu weit voneinander entfernt
- Gerät nicht eingeschaltet
- Dicke Mauern

### 4. Spannungsversorgung

Netzbetrieb:
Beide Geräte können mit einem handelsüblichen 5 V USB-Netzteil und einem USB-C-Kabel mit Spannung (+ 5 V) versorgt und betrieben werden.

Akkubetrieb:

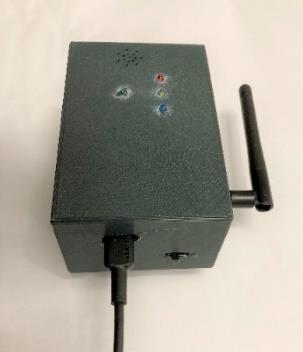
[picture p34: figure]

Wenn in den Geräten ein Li-Ionen-Akku der Type 18650 mit 3,7 V eingebaut ist, können die Geräte über den Akku betrieben werden. Für eine Akkulaufzeit von 1 Woche wird ein Li-Ionen-Akku mit einer Kapazität von mindestens 4500 mAh benötigt.

Laden des Akkus:
Ist in den Geräten ein Akku eingebaut, so wird dieser automatisch geladen, wenn das Gerät über ein USB-C-Kabel mit Spannung versorgt wird. Der Akku wird mit einem maximalen Ladestrom von 1 A geladen. Das vollständige Laden eines 4500 mAh großen Akkus dauert in etwa 4,5 Stunden.

Wird bei geöffnetem Gehäuse der Akku geladen,so leuchtet auf der Platine eine rote LED (Bezeichnung D5) und wenn der Ladevorgang abgeschlossen ist, leuchtet eine weiße LED (Bezeichnung D6).

Tausch des Akkus:

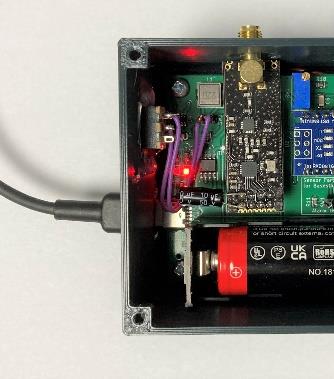
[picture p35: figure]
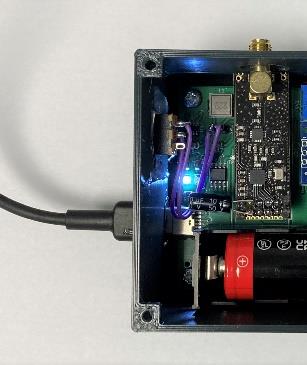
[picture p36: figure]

Um den eingebauten Akku zu tauschen, muss zuerst der Boden der Geräte abgeschraubt werden. Dazu wird ein Kreuzschlitzschraubendreher der Größe PZ1 benötigt. Danach kann der Akku entnommen werden. Der Akku muss so eingesetzt werden, dass dessen Pluspol, wie im Bild unten, auf der Seite des Ein- und Ausschalters ist, damit es nicht zu einer Verpolung kommt.

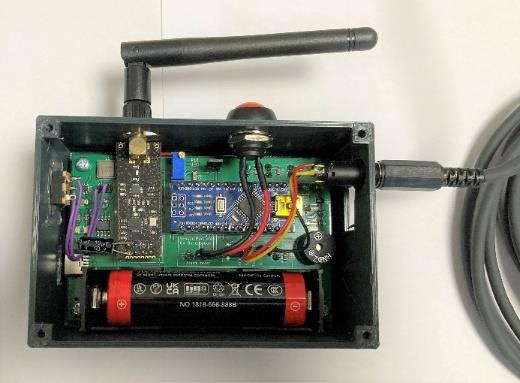
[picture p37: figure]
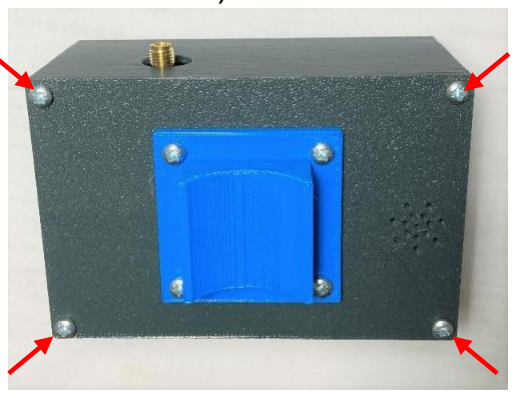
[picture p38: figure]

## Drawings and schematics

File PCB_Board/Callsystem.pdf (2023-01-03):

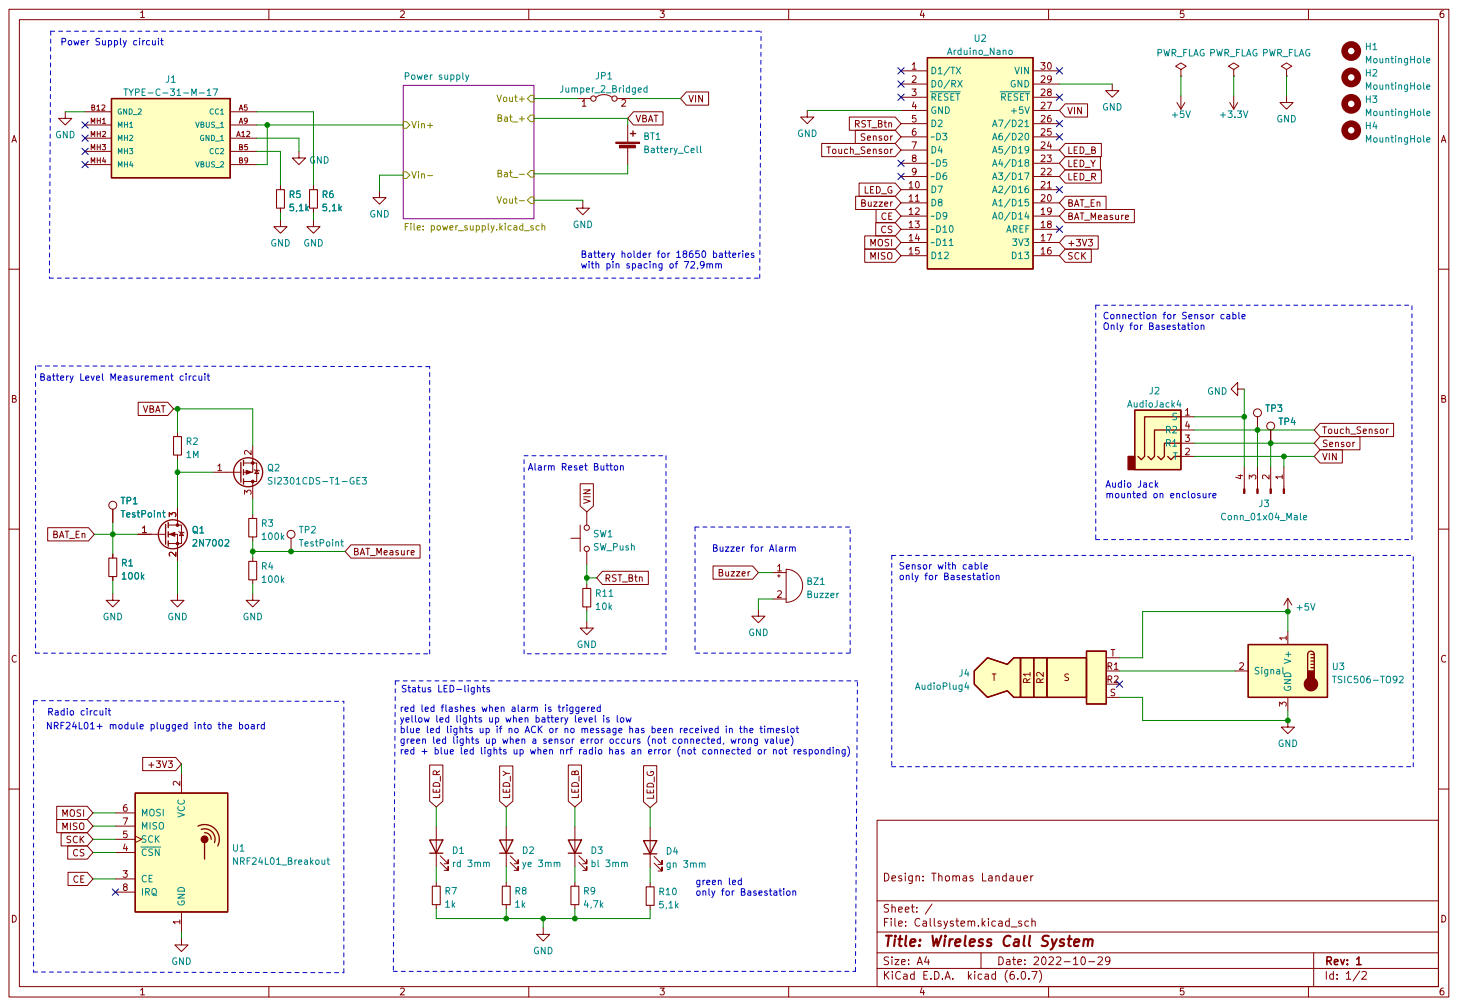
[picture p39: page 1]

Battery holder for 18650 batteries
with pin spacing of 72,9mm

Status LED-lights
red led flashes when alarm is triggered
yellow led lights up when battery level is low
blue led lights up if no ACK or no message has been received in the timeslot
green led lights up when a sensor error occurs (not connected, wrong value)
red + blue led lights up when nrf radio has an error (not connected or not responding)

NRF24L01+ module plugged into the board

2 CE 3 ~{CSN} 4 SCK 5 MOSI 6 MISO 7
SCKCSCE MISO

File: Callsystem.kicad_sch Sheet: / Design: Thomas Landauer

Id: 1/2 Title: Wireless Call System

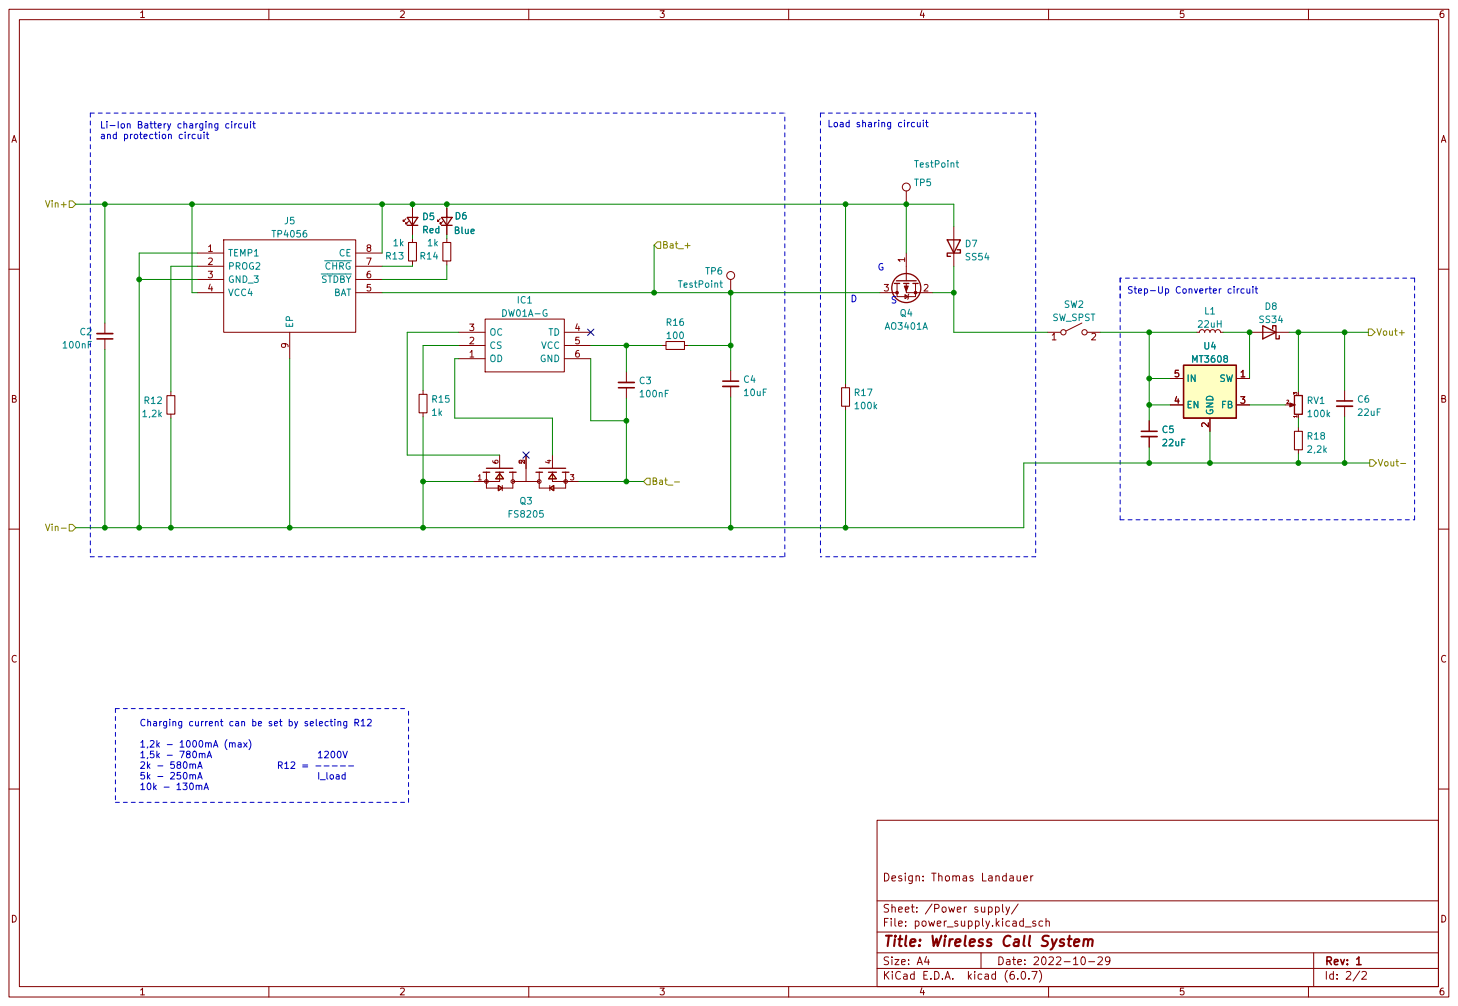
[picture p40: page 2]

Li-Ion Battery charging circuit
and protection circuit

Step-Up Converter circuit S G

4 Q3 FS8205 OD 1 CS 2 OC 3 TD 4 VCC 5 GND 6

Sheet: /Power supply/
File: power_supply.kicad_sch
Id: 2/2 Title: Wireless Call System

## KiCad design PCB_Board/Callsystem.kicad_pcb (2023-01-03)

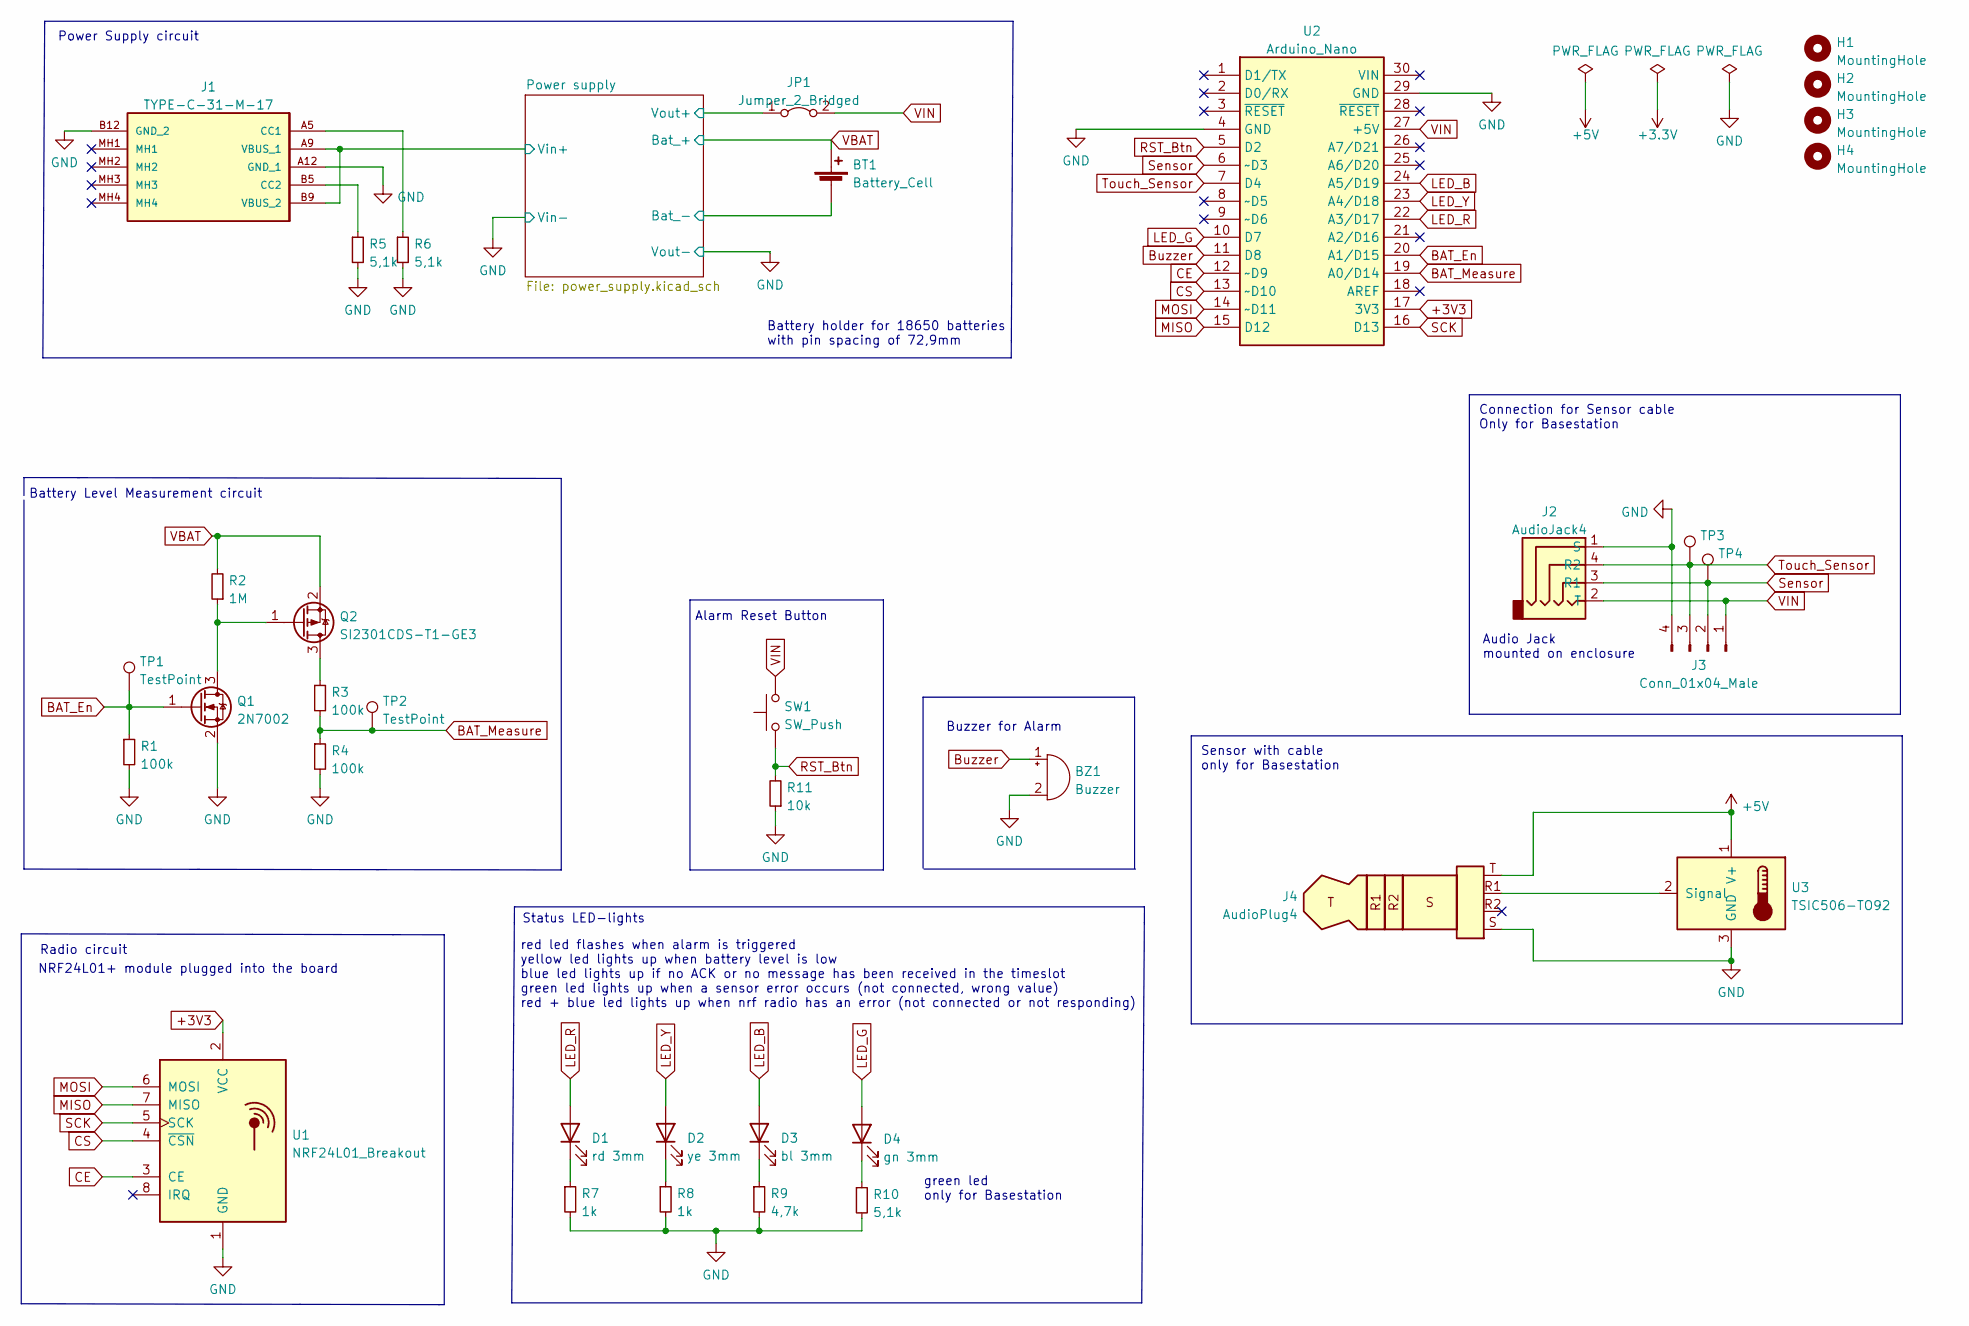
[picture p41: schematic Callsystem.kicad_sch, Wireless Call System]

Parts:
BT1: Battery_Cell; BatteryHolder_MPD_BH-18650-PC2
BZ1: Buzzer; Buzzer_12x9.5RM7.6; LCSC C96222
D1: rd 3mm; PinHeader_1x02_P2.54mm_Vertical; LCSC C234182
D2: ye 3mm; PinHeader_1x02_P2.54mm_Vertical; LCSC C234182
D3: bl 3mm; PinHeader_1x02_P2.54mm_Vertical; LCSC C234182
D4: gn 3mm; PinHeader_1x02_P2.54mm_Vertical; LCSC C234182
H1, H2, H3, H4: MountingHole; MountingHole_3.2mm_M3
J1: TYPE-C-31-M-17; TYPEC31M17_new; MANUFACTURER_PART_NUMBER TYPE-C-31-M-17; LCSC C283540
J2: AudioJack4; PinHeader_1x04_P2.54mm_Vertical
J3: Conn_01x04_Male; PinHeader_1x04_P2.54mm_Vertical; LCSC C2905435
J4: AudioPlug4
JP1: Jumper_2_Bridged; PinHeader_1x02_P2.54mm_Vertical; LCSC C234182
Q1: 2N7002; SOT-23; LCSC C8545
Q2: SI2301CDS-T1-GE3; SOT-23; LCSC C10487
R1, R3, R4: 100k; R_0805_2012Metric; LCSC C149504
R2: 1M; R_0805_2012Metric; LCSC C17514
R5, R6, R10: 5,1k; R_0805_2012Metric; LCSC C27834
R7, R8: 1k; R_0805_2012Metric; LCSC C17513
R9: 4,7k; R_0805_2012Metric; LCSC C17673
R11: 10k; R_0805_2012Metric; LCSC C17414
SW1: SW_Push; PinHeader_1x02_P2.54mm_Vertical; LCSC C234182
TP1, TP2, TP3, TP4: TestPoint; TestPoint_Pad_D1.0mm
U1: NRF24L01_Breakout; nRF24L01_LNA_Module; LCSC C239344
U2: Arduino_Nano
U3: TSIC506-TO92; TO-92_Inline

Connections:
+3V3: U1.2 (VCC), U2.17 (3V3)
/Power supply/Bat_-: BT1.2 (-); also elsewhere on the board
/Power supply/Vin+: J1.A9 (VBUS_1), J1.B9 (VBUS_2); also elsewhere on the board
/Power supply/Vout+: JP1.1 (A); also elsewhere on the board
BAT_En: Q1.1 (G), R1.1, TP1.1, U2.20 (A1/D15)
BAT_Measure: R3.2, R4.1, TP2.1, U2.19 (A0/D14)
Buzzer: BZ1.1 (-), U2.11 (D8)
CE: U1.3 (CE), U2.12 (~D9)
CS: U1.4 (~CSN), U2.13 (~D10)
GND: BZ1.2 (+), J1.A12 (GND_1), J1.B12 (GND_2), J2.1 (S), J3.4, J4.S, Q1.2 (S), R1.2, R4.2, R5.2, R6.2, R7.2, R8.2, R9.2, R10.2, R11.1, U1.1 (GND), U2.4 (GND), U2.29 (GND), U3.3 (GND); also elsewhere on the board
LED_B: D3.2 (A), U2.24 (A5/D19)
LED_G: D4.2 (A), U2.10 (D7)
LED_R: D1.2 (A), U2.22 (A3/D17)
LED_Y: D2.2 (A), U2.23 (A4/D18)
MISO: U1.7 (MISO), U2.15 (D12)
MOSI: U1.6 (MOSI), U2.14 (~D11)
unnamed: D1.1 (K), R7.1
unnamed: D2.1 (K), R8.1
unnamed: D3.1 (K), R9.1
unnamed: D4.1 (K), R10.1
unnamed: J1.A5 (CC1), R6.1
unnamed: J1.B5 (CC2), R5.1
unnamed: J4.R1, U3.2 (Signal)
unnamed: J4.T, U3.1 (V+)
unnamed: Q1.3 (D), Q2.1 (G), R2.1
unnamed: Q2.3 (D), R3.1
RST_Btn: R11.2, SW1.1, U2.5 (D2)
SCK: U1.5 (SCK), U2.16 (D13)
Sensor: J2.3 (R1), J3.2, TP4.1, U2.6 (~D3)
Touch_Sensor: J2.4 (R2), J3.3, TP3.1, U2.7 (D4)
VBAT: BT1.1 (+), Q2.2 (S), R2.2; also elsewhere on the board
VIN: J2.2 (T), J3.1, JP1.2 (B), SW1.2, U2.27 (+5V)

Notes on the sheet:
Radio circuit
Status LED-lights
Buzzer for Alarm
red led flashes when alarm is triggered yellow led lights up when battery level is low blue led lights up if no ACK or no message has been received in the timeslot green led lights up when a sensor error occurs (not connected, wrong value) red + blue led lights up when nrf radio has an error (not c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
NRF24L01+ module plugged into the board
Battery Level Measurement circuit
Sensor with cable only for Basestation
Battery holder for 18650 batteries with pin spacing of 72,9mm
Audio Jack mounted on enclosure
Power Supply circuit
green led only for Basestation
Connection for Sensor cable Only for Basestation
Alarm Reset Button

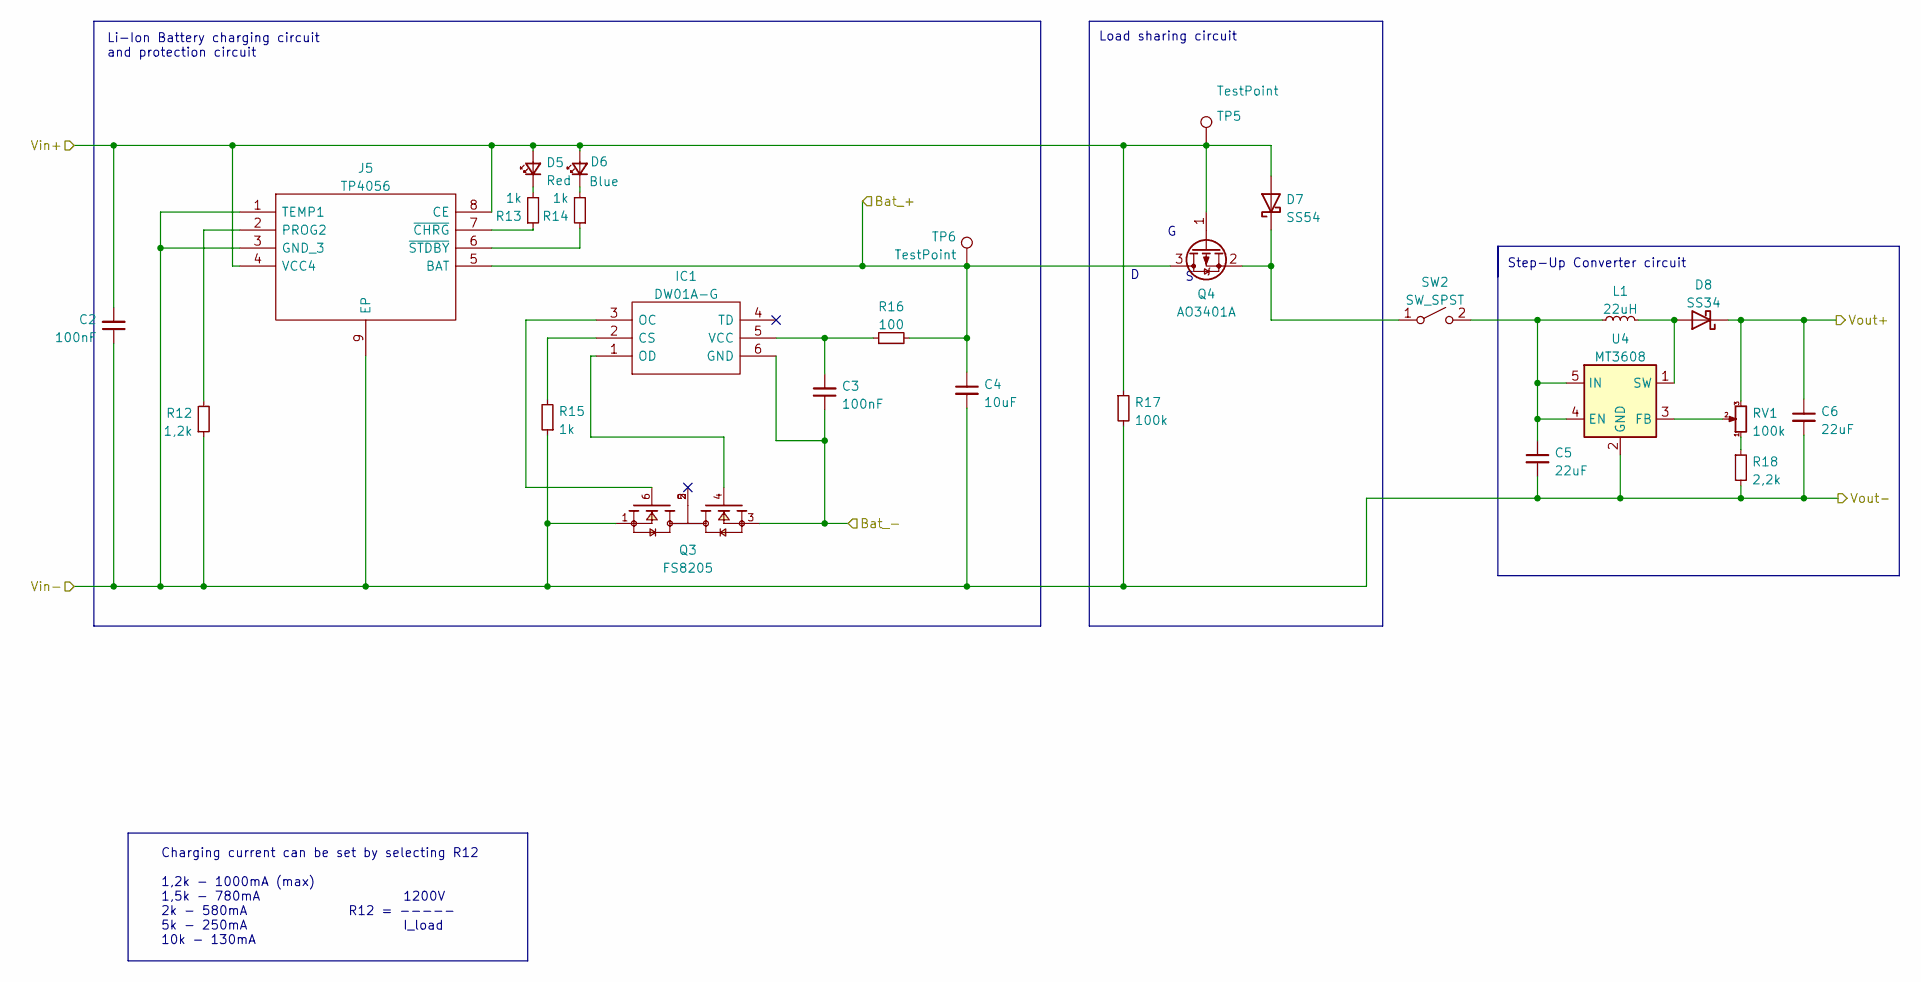
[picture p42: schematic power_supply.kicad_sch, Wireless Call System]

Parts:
C2, C3: 100nF; C_0805_2012Metric; LCSC C49678
C4: 10uF; C_0805_2012Metric; LCSC C15850
C5, C6: 22uF; C_1206_3216Metric; LCSC C12891
D5: Red; LED_0805_2012Metric; LCSC C84256
D6: Blue; LED_0805_2012Metric; LCSC C34499
D7: SS54; D_SMA; LCSC C22452
D8: SS34; D_SMA; LCSC C8678
IC1: DW01A-G; SOT-23-6; Manufacturer_Part_Number DW01A-G; LCSC C61503
J5: TP4056; SOP127P600X175-9N; Manufacturer_Part_Number TP4056; LCSC C16581
L1: 22uH; SLO0630H; LCSC C207843
Q3: FS8205; SOT-23-6; PARTREV 1.9; LCSC C908265
Q4: AO3401A; SOT-23; LCSC C15127
R12: 1,2k; R_0805_2012Metric; LCSC C17379
R13, R14, R15: 1k; R_0805_2012Metric; LCSC C17513
R16: 100; R_0805_2012Metric; LCSC C17408
R17: 100k; R_0805_2012Metric
R18: 2,2k; R_0805_2012Metric; LCSC C17520
RV1: 100k; Potentiometer_Bourns_3296W_Vertical; LCSC C118963
SW2: SW_SPST; PinHeader_1x02_P2.54mm_Vertical; LCSC C234182
TP5, TP6: TestPoint; TestPoint_Pad_D1.0mm
U4: MT3608; SOT-23-6; LCSC C84817

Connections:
/Power supply/Bat_-: C3.1, IC1.6 (GND), Q3.3; also elsewhere on the board
/Power supply/Vin+: C2.2, D5.2 (A), D6.2 (A), D7.2 (A), J5.4 (VCC4), J5.8 (CE), Q4.1 (G), R17.1, TP5.1; also elsewhere on the board
/Power supply/Vout+: C6.1, D8.1 (K), RV1.3; also elsewhere on the board
GND: C2.1, C4.2, C5.2, C6.2, J5.1 (TEMP1), J5.3 (GND_3), J5.9 (EP), Q3.1, R12.1, R15.1, R17.2, R18.2, U4.2 (GND); also elsewhere on the board
unnamed: C3.2, IC1.5 (VCC), R16.1
unnamed: C5.1, L1.1, SW2.2 (B), U4.4 (EN), U4.5 (IN)
unnamed: D5.1 (K), R13.2
unnamed: D6.1 (K), R14.2
unnamed: D7.1 (K), Q4.2 (S), SW2.1 (A)
unnamed: D8.2 (A), L1.2, U4.1 (SW)
unnamed: IC1.1 (OD), Q3.4
unnamed: IC1.2 (CS), R15.2
unnamed: IC1.3 (OC), Q3.6
unnamed: J5.2 (PROG2), R12.2
unnamed: J5.6 (~STDBY), R14.1
unnamed: J5.7 (~CHRG), R13.1
unnamed: R18.1, RV1.1
unnamed: RV1.2, U4.3 (FB)
VBAT: C4.1, J5.5 (BAT), Q4.3 (D), R16.2, TP6.1; also elsewhere on the board

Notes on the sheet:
Load sharing circuit
Charging current can be set by selecting R12 1,2k - 1000mA (max) 1,5k - 780mA 2k - 580mA 5k - 250mA 10k - 130mA
Step-Up Converter circuit
Li-Ion Battery charging circuit and protection circuit
1200V R12 = ----- I_load

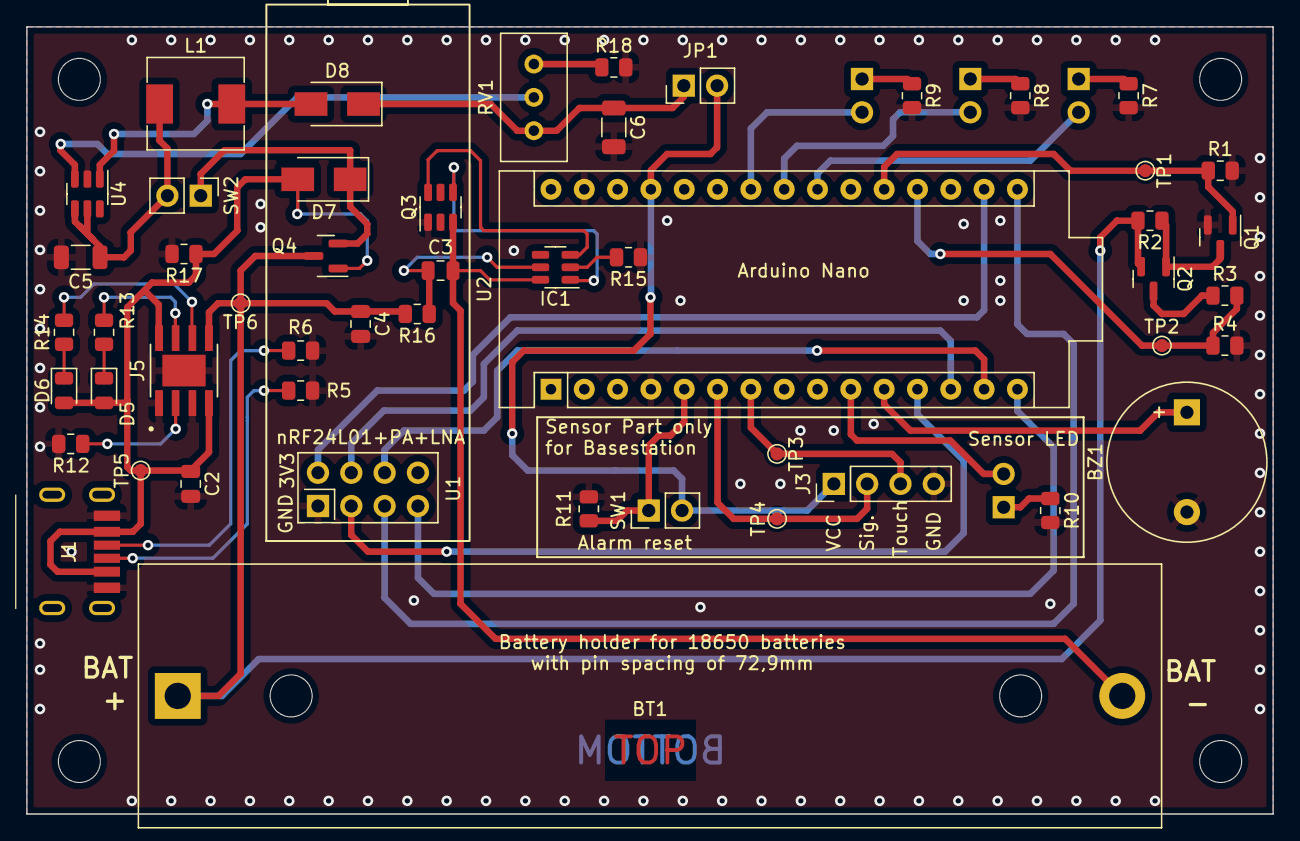
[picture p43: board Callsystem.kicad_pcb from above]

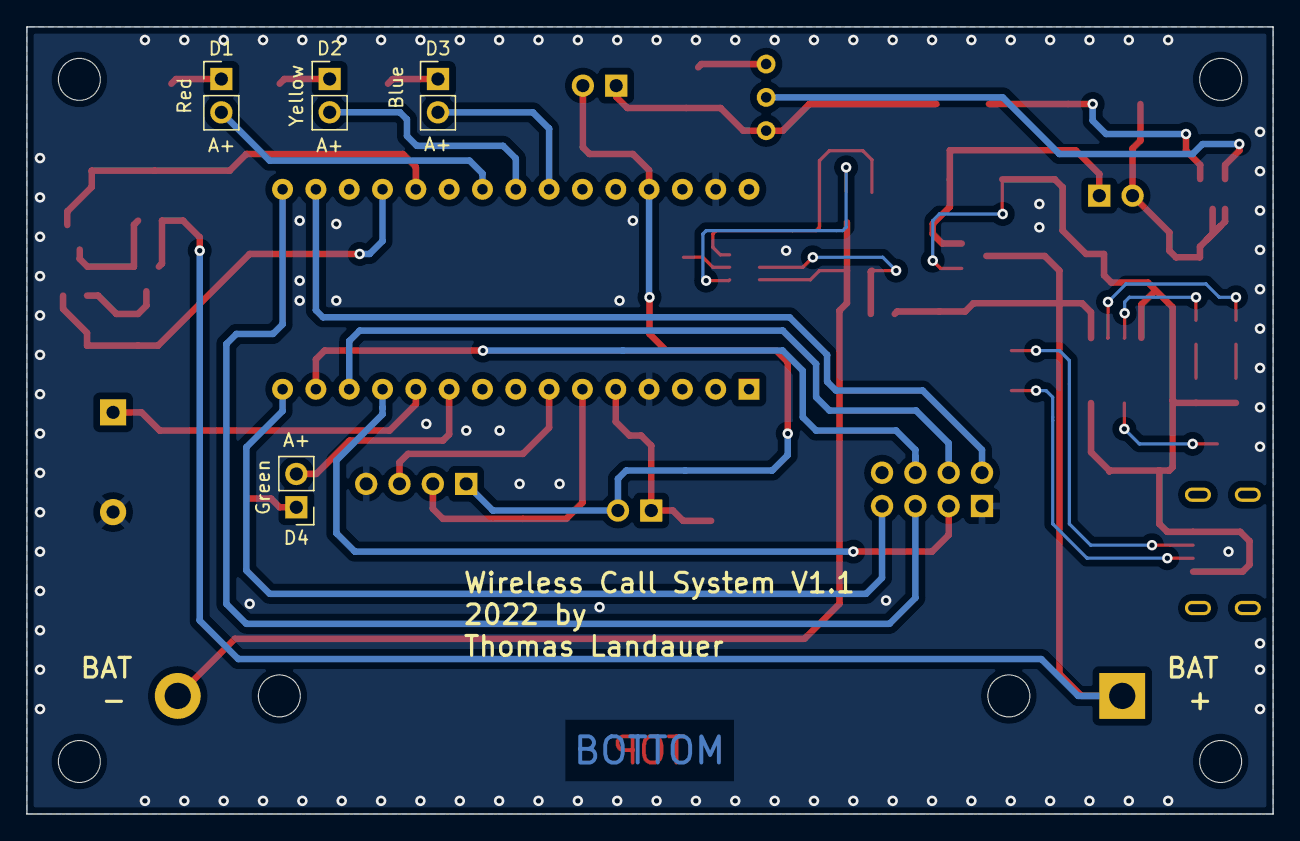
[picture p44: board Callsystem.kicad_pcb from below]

Board: 2 copper layers, 95.0 x 60.0 mm, 59 parts (4 on the bottom side), 44 nets.

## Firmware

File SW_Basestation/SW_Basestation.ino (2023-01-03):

/*
 * Firmware for running the basestation of the wirless controlled nurse call system
 * This Firmware was only tested with an Arduino Nano.
 *
 * Version 1.0 (by Thomas Landauer, 2022.11.09)
 *
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
 * You should have received a copy of the GNU General Public License
 * along with this program.  If not, see <http://www.gnu.org/licenses/>.
 */

#include "src/TSic.h" // library inside src folder
#include <Arduino.h>
#include <RF24.h> // library for nRF24L01 Transceiver
#include <avr/power.h> // library to en- or disable components like i2c or timer
#include <avr/sleep.h>
#include <math.h>

#define USE_SLEEP 1 // set to 1 for Arduino sleep function (if enabled, DEBUG and NRFDEBUG will not work properly)
#define DEBUG 0 // set to 1 to print debug messages (slows down execution)
#define NRFDEBUG 0 // set to 1 to print nrf specific debug messages (slows down execution)
#define NRFSENDINTERVAL 25 // defines send interval of nrf-module; multiple times of 4ms (100ms=25*4ms)

#define NUMOFBLINKS 3 // sets the number of flashes after successful initialisation
#define BLINKINTERVAL 500 // sets the flashing interval after successful initialisation (1=1ms)
#define ALARMBLINKINTERVAL 62 // defines alarm blink interval; multiple times of 4ms (248ms=62*4ms)
#define BATTERYCHKINTERVAL 300 // define battery check period; multiple times of 1s (1min = 60*1s)
#define NUM_SAMPLES 10 // defines number of ADC samples for battery voltage measurement
#define BATTERYTHRESHOLD 3.0 // defines the threshold for an empty battery
#define USEBUZZER 1 // set to 1 to enable Buzzer Audio output

#if DEBUG == 1
#define debug(x) Serial.print(x)
#define debugln(x) Serial.println(x)
#else
#define debug(x)
#define debugln(x)
#endif
#if NRFDEBUG == 1
#define nrfdebug(x) Serial.print(x)
#define nrfdebugln(x) Serial.println(x)
#else
#define nrfdebug(x)
#define nrfdebugln(x)
#endif

// timer variables
volatile uint16_t nrf_timing = 0;
volatile uint16_t alarm_timing = 0;
volatile uint16_t battery_timing = 0;

// Pin for Reset button
const int ResetButton = 2;

// TSic506 Variables
const uint8_t TSic_Pin = 3; // Signal Pin of TSIC-Sensor
TSIC Sensorx(TSic_Pin);
volatile float TSic_temp = NAN; // Temperature in °C
volatile bool TSic_newData = 0; // flag to indicate new data
volatile uint8_t TSic_isrCount = 0; // TSic_isrCount for error check
float temp_val[2] = { NAN, NAN };
float dT_val[2] = { NAN, NAN };
float alarm_sensitivity = 0.04;

// indicator LEDs - active High
const int led_red = 17;
const int led_yellow = 18;
const int led_blue = 19;
const int led_green = 7; // correct to 7
// Buzzer pin
const int Buzzer = 8;

// Variables for Battery measurement
const int Bat_measure = A0; // Analog Pin A0
const int Bat_En = 15; // Digital Pin 15
float battery_voltage = 0;

// Error values
volatile bool nrf_error = 0;
volatile bool nrf_ack_error = 0;
volatile bool TSic_error = 0;
volatile bool Alarm_flag = 0;

// variables for nRF24 Transceiver
// creating a new instance for tranceiver called radio
RF24 radio(9, 10); // CE-Pin, CSN-Pin
const byte PairAddress[6] = "Nurse"; // define address for communicating
char payload[10] = "Sync Msg 0";
// debug variables
volatile uint32_t sleeptimebegin = 0;
volatile uint32_t previoustime = 0;
volatile uint32_t currenttime = 0;

void setup()
{
    // Initialisation of the GPIO-Pins
    pinMode(led_red, OUTPUT);
    pinMode(led_yellow, OUTPUT);
    pinMode(led_blue, OUTPUT);
    pinMode(led_green, OUTPUT);
    pinMode(Bat_En, OUTPUT);
    pinMode(Buzzer, OUTPUT);

    digitalWrite(Buzzer, LOW);
    digitalWrite(led_red, LOW);
    digitalWrite(led_yellow, LOW);
    digitalWrite(led_blue, LOW);
    digitalWrite(led_green, LOW);
    digitalWrite(Bat_En, LOW);

    // Initialisation of ResetButton Pin
    pinMode(ResetButton, INPUT_PULLUP);

#if (NRFDEBUG == 1) || (DEBUG == 1) // Opens the serial interface only if debug options are set.
    Serial.begin(115200);
#endif

    // clear pending interrupts before attachInterrupt()
    EIFR = (1 << INTF0); // clear interrupt 0 flag
    EIFR = (1 << INTF1); // clear interrupt 1 flag

    // begin initialisation of nrf transceiver
    if (!Nrf_Init()) {
        debugln("nrf init ok---------");
        radio.powerDown();
    } else {
        // Initialisation failed - hardware reset required
        // nrf-radio module needs hardware reset to operate properly
        // code stops working here
        nrf_error = 1;
        Error_handle();
    }

    // allow external interrupts on the defined pins
    attachInterrupt(digitalPinToInterrupt(ResetButton), ISR_reset_button, FALLING);
    attachInterrupt(digitalPinToInterrupt(TSic_Pin), TSic_isr, FALLING);

    // now wait for a correct sensor value
    // If the value is incorrect, switch on the green LED
    TSic_error = 1;
    while (1) {
        if (TSic_newData == 1) {
            TSic_newData = 0;
            TSic_error = Tsic_ErrorCheck(&TSic_temp);
            if (TSic_error == 0) {
                Error_handle();
                break;
            }
            Error_handle();
        }
        Error_handle();
    }
    // Init finished and all LEDs flash x times
    blink_all_leds(NUMOFBLINKS, BLINKINTERVAL);
    debugln("init finish"); // for testing purpose
    currenttime = 0;
    previoustime = 0;
    timer2_init(); // Starting timer 2
}

void loop()
{
    // code starts here after sleep

    // true if new Temperature data is available and if no alarm is set
    if (TSic_newData == 1 && Alarm_flag == 0) {
        TSic_newData = 0;
        TSic_error = Tsic_ErrorCheck(&TSic_temp); // Checks if Data is a valid number
        Error_handle();
        Alarm_flag = Alarmdetection(); // Check if alarm condition has been reached
        if (Alarm_flag == 1) // set the alarm immediately
        {
            digitalWrite(led_red, HIGH);
#if USEBUZZER == 1
            digitalWrite(Buzzer, HIGH);
#endif
            alarm_timing = 0;
        }
    }

    // Starts the transmission process to the handheld
    if (nrf_timing >= NRFSENDINTERVAL) // true every ___ms=NRFSENDINTERVAL * 4ms
    {
        nrf_timing = 0; // reset time counter
        previoustime = currenttime;
        currenttime = millis();
        nrfdebugln("_________________");
        nrfdebug(currenttime - sleeptimebegin);
        nrfdebugln("ms sleeped");
        nrfdebug(currenttime - previoustime);
        nrfdebugln("ms between 2 wakeups");

        // Checks if sensor is connected.
        // If TSIC-ISR has not been executed since the last transmission, the sensor is not connected.
        if (Alarm_flag == 0) {
            if (TSic_isrCount == 0) {
                TSic_error = 1; // sensor not connected!
            } else {
                TSic_isrCount = 0;
            }
        }
        Error_handle();
        // wakes up nrf-module from sleep
        // takes up to approx. 20ms for power up
        radio.powerUp();
        Nrf_Init();

        nrf_error = !radio.isChipConnected(); // checks if the module is connected to the SPI bus
        if (nrf_error == 1) {
            Error_handle();
        }
        // The payload is selected depending on the flag set.
        if (Alarm_flag == 1) {
            strncpy(payload, "ALARM", 10);
        } else {
            if (TSic_error == 1) {
                strncpy(payload, "TSIC_err", 10);
            } else {
                strncpy(payload, "SYNC", 10);
            }
        }
        nrfdebug("payload:");
        nrfdebugln(payload);
        // Sends the message and waits for an acknowledge from the handheld.
        // The Auto ACK feature of the NRF module is used.
        if (radio.write(&payload, sizeof(payload))) {
            nrfdebugln("ACK received");
            nrfdebugln("_________");
            nrf_ack_error = 0;
        } else {
            nrfdebugln("TX failed");
            nrfdebugln("_________");
            nrf_ack_error = 1;
        }
        // puts nrf-module into sleep
        radio.powerDown();
        Error_handle();
    }

    // Battery Voltage check
    if (battery_timing >= BATTERYCHKINTERVAL) // true every BATTERYCHKINTERVAL*1sec
    {
        battery_timing = 0; // reset time counter
        battery_voltage = Battery_measurement(Bat_En, Bat_measure, NUM_SAMPLES); // measures the voltage of the battery
        debug("Battery Voltage [V]:");
        debugln(battery_voltage);
        if (battery_voltage <= BATTERYTHRESHOLD) // True if the battery voltage is below the limit value
        {
            // turn the ledPin on
            digitalWrite(led_yellow, HIGH);
            debugln("Battery Low");
        } else {
            digitalWrite(led_yellow, LOW);
            debugln("Battery normal condition");
        }
    }

#if USE_SLEEP == 1
    EnterSleep(); // Put the Arduino in sleep mode to save energy
#endif
}

/*
Saves the new temperature value and checks if there is an alarm.
The function returns 1 if the alarm condition is fulfilled and 0 if not.
The alarm condition is fulfilled if the temperature rise dT of 2 values
is valid and their average value exceeds the set limit value and the temperature
trend goes in the same direction (positive or negative), then the alarm is triggered.
*/
bool Alarmdetection()
{
    // store old val in temp_val[0]
    // store new val in temp_val[1]
    debugln("______________________");
    debug("old temp_val[0]: ");
    debugln(temp_val[0]);
    temp_val[0] = temp_val[1];
    temp_val[1] = TSic_temp;
    debug("temp_val[0]: ");
    debugln(temp_val[0]);
    debug("temp_val[1]: ");
    debugln(temp_val[1]);
    // check if stored temperature values are valid numbers
    // if valid numbers store old dT_value in dT_val[0] and new value in dT_val[1]
    if (isnan(temp_val[0]) || isnan(temp_val[1])) {
        dT_val[1] = NAN;
    } else {
        dT_val[0] = dT_val[1];
        dT_val[1] = temp_val[1] - temp_val[0];
    }
    debug("dT_val[0]: ");
    debugln(dT_val[0]);
    debug("dT_val[1]: ");
    debugln(dT_val[0]);
    // do further processing only if dT_values are valid (not NAN)
    if (!isnan(dT_val[0]) || !isnan(dT_val[1])) {
        // check if absolute value of both dT_values is greater than the threshold value
        if ((abs(dT_val[0]) > alarm_sensitivity) && (abs(dT_val[1]) > alarm_sensitivity)) {

            // now check wether both values have a positive or negative tendency and only then set alarm
            if ((dT_val[0] > 0 && dT_val[1] > 0) || dT_val[0] < 0 && dT_val[1] < 0) {
                debugln("ALARM >>>> 0");
                debugln("______________________");
                return 1; // Set alarm
            }
        }
    }
    return 0;
}

// Checks if Temperaturdata is a valid number
bool Tsic_ErrorCheck(float* Tempdata)
{
    if (isnan(*Tempdata)) // isnan()returns 1 if value is NaN -> error reading sensor
    {
        return 1;
    } else {
        return 0;
    }
}

// puts the Arduino into the defined sleep mode
void EnterSleep(void)
{
    set_sleep_mode(SLEEP_MODE_EXT_STANDBY);
    cli(); // deactivate interrupts
    sleep_enable(); // sets the SE (sleep enable) bit
    // sleep_bod_disable(); // disable Brown Out Detector (~60us faster resume to aktive )
    sei(); // enable interrupts
    sleep_cpu(); // sleep now!!
    sleep_disable(); // deletes the SE bit
}
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

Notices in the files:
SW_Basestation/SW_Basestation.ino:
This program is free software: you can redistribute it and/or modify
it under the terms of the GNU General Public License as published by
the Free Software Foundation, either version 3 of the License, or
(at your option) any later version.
